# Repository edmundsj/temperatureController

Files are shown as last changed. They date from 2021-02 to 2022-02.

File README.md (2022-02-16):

# TEC Temperature Controller PCB
This PCB is designed to monitor and control the temperature of an object heated or cooled with a thermoelectric cooler (TEC), and is capable of driving up to 8A

## Features
- TEC temperature regulation within 0.1C using PI control
- Max TEC Voltage/current of 3.6V/6A when powered off 5V
- 1% settling time of ~90s 
- Bidirectional temp. control (heating and cooling) 
- 6A max current with 8-bit current monitoring (~25mA accuracy)
- Computer-independent measurement and temperature control using on-board interface
- Can be powered over USB (current limited by driving source)
- Closed-loop control of temperature using MCP9808 remote temperature sensor
- Two 3-digit 7-segment displays for temperature setpoint and measured value
- Knob potentiometer for setting target temperature
- Passive cooling (~4K/W thermal resistance) with 1.5" radial heatsink
- Arduino nano-based

Populated PCB
Fully populated PCB

Unpopulated PCB
Unpopulated, as-fabricated PCB

## Getting Started
Kicad design files for this PCB are located in the ``kicad/`` folder. Gerbers
can be generated directly for fabrication, or you can find the latest gerbers
in the ``gerbers/`` directory. The parts required can be found in ``bom.csv``.
Software can be found in the ``controller_software/`` directory, which can be
copied to your local machine, and uploaded to an Arduino nano via the Arduino
IDE. This system is rated to work at 5V, so make sure the power adapter used is
rated for 5V, and as much current as is required. For the TEC I built this
system around, that is ~6A.

## Issues
### Issues in Version 1
- [FIXED v2] Need VDD, GND connections on header going to MCP9808 board in addition to SDA and SCL.
- [FIXED v2] Need to make sure the ordering and connector matches that of the device PCB.
- [FIXED v2] In the future, a couple of accessible header GND connections would be nice, even just for probing.
- [FIXED v2] Should edit the silkscreen to include the directionality of the Arduino Nano's USB. 
- [FIXED v2] Should swap out MOSFET for a more linear BJT
- [FIXED v2] Swap out MOSFET for transistor with much lower thermal resistance
- [FIXED v2] My choice of resistor is not sufficient, the thing heats up and starts to smoke after a couple seconds at ~5A. 

### Issues in Version 2
- [FIXED v3] R4 is too close to the heatsink, difficult to access. Moved.
- [FIXED v3] Added capacitor for filtering of input drive voltage
- [FIXED v3] Added 2x2 ground header pins for probing
- [FIXED v3] Added relay with drive transistor to allow bidirectional current flow through TEC
- [FIXED v3] Added silkscreen + courtyard + mounting holes for main heatsink
- [FIXED v3] Current sensing is unreliable due to ADC being near rails, added opamp buffer + biasing

### Issues in Version 3
- Standoffs should be as far to the outside to avoid tipping the board when using screw terminals
- Need to add test piont for VDR_F. 
- C4 should be removed. We have no business filtering a voltage going to the base of the BJT.
- Add probe points for communication interface for easier debugging. 
- Add probe points for ground silkscreen
- Decouple VDD of arduino and TEC.

## Acknowledgements

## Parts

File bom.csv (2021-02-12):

Verision | Part Name | Quantity | Source | Catalog Number | Link
2 | 8.5A TEC | 1 | Digikey | 345-1740-ND | https://www.digikey.com/product-detail/en/TEC-20-33-31/345-1740-ND/9741968/?itemSeq=349654408
2 | Power NPN | 1 | Digikey | BDW42GOS-ND | https://www.digikey.com/product-detail/en/BDW42G/BDW42GOS-ND/1476196/?itemSeq=350783096
2 | 3-digit 7-segment display | 2 | Digikey | 160-1545-5-ND | https://www.digikey.com/product-detail/en/LTC-4724JR/160-1545-5-ND/408218/?itemSeq=349666458
2 | MAX7219 Display Driver | 1 | Digikey | MAX7219CWG+TCT-ND | https://www.digikey.com/product-detail/en/MAX7219CWG%2bT/MAX7219CWG%2bTCT-ND/4146791/?itemSeq=349667061
2 | Power Jack | 1 | Digikey | 839-54-00167-ND | https://www.digikey.com/product-detail/en/54-00167/839-54-00167-ND/10459295/?itemSeq=349668384
2 | Temp-Sensing IC | 1 | Digikey | 1597-1651-ND | https://www.digikey.com/product-detail/en/101020556/1597-1651-ND/9369931/?itemSeq=349671089
2 | 10K Pot | 1 | Digikey | 987-1710-ND | https://www.digikey.com/product-detail/en/P120PK-Y25BR10K/987-1710-ND/5957454/?itemSeq=349673044
2 | 2POS Screw Terminal | 1 | Digikey | 732-10955-ND | https://www.digikey.com/product-detail/en/691137710002/732-10955-ND/6644051/?itemSeq=349675219
2 | 0.2Ohm power sense resistor | 1 | Digikey | 696-1162-ND | https://www.digikey.com/product-detail/en/PF2203-0R2F1/696-1162-ND/2447810/?itemSeq=349699745
2 | Nano Headers | 2 | Digikey | S7013-ND | https://www.digikey.com/product-detail/en/PPTC151LFBN-RC/S7013-ND/810153/?itemSeq=349713274
2 | TO-220 Heatsink | 1 | Digikey | HS350-ND | https://www.digikey.com/product-detail/en/529802B02500G/HS350-ND/1216357/?itemSeq=350783079
2 | Standoff Pins | 4 | Digikey | 36-25501-ND | https://www.digikey.com/product-detail/en/25501/36-25501-ND/1532180/?itemSeq=350475444
3 | NMOS Transistor | 1 | Digikey | DMN63D8LW-13DICT-ND | https://www.digikey.com/en/products/detail/diodes-incorporated/DMN63D8LW-13/5722399
3 | 5V, 8A, 62R Relay | 1 | Digikey | G2RL-2-DC5 | https://www.digikey.com/en/products/detail/omron-electronics-inc-emc-div/G2RL-2-DC5/1789837?s=N4IgTCBcDaIOJgEoBkC0ZUBEDCBWEAugL5A
3 | MCP Dual Opamp | 1 | Digikey | MCP6L02T-E/SNCT-ND_ | https://www.digikey.com/product-detail/en/MCP6L02T-E%2fSN/MCP6L02T-E%2fSNCT-ND/2060115/?itemSeq=352014804
3 | 6Pos SMD Header | 1 | Digikey | 455-2264-1-ND | https://www.digikey.com/product-detail/en/jst-sales-america-inc/S6B-XH-SM4-TB(LF)(SN)/455-2264-1-ND/1651062
3 | 10uF 0805 cap | 3 | Digikey
3 | 100vF 0805 cap | 2 | Digikey
3 | 10k 0805 Resistor | 6 | Digikey
3 | 1k 0805 Res | 1 | Digikey
3 | 30k 0805 Res | 1 | Digikey

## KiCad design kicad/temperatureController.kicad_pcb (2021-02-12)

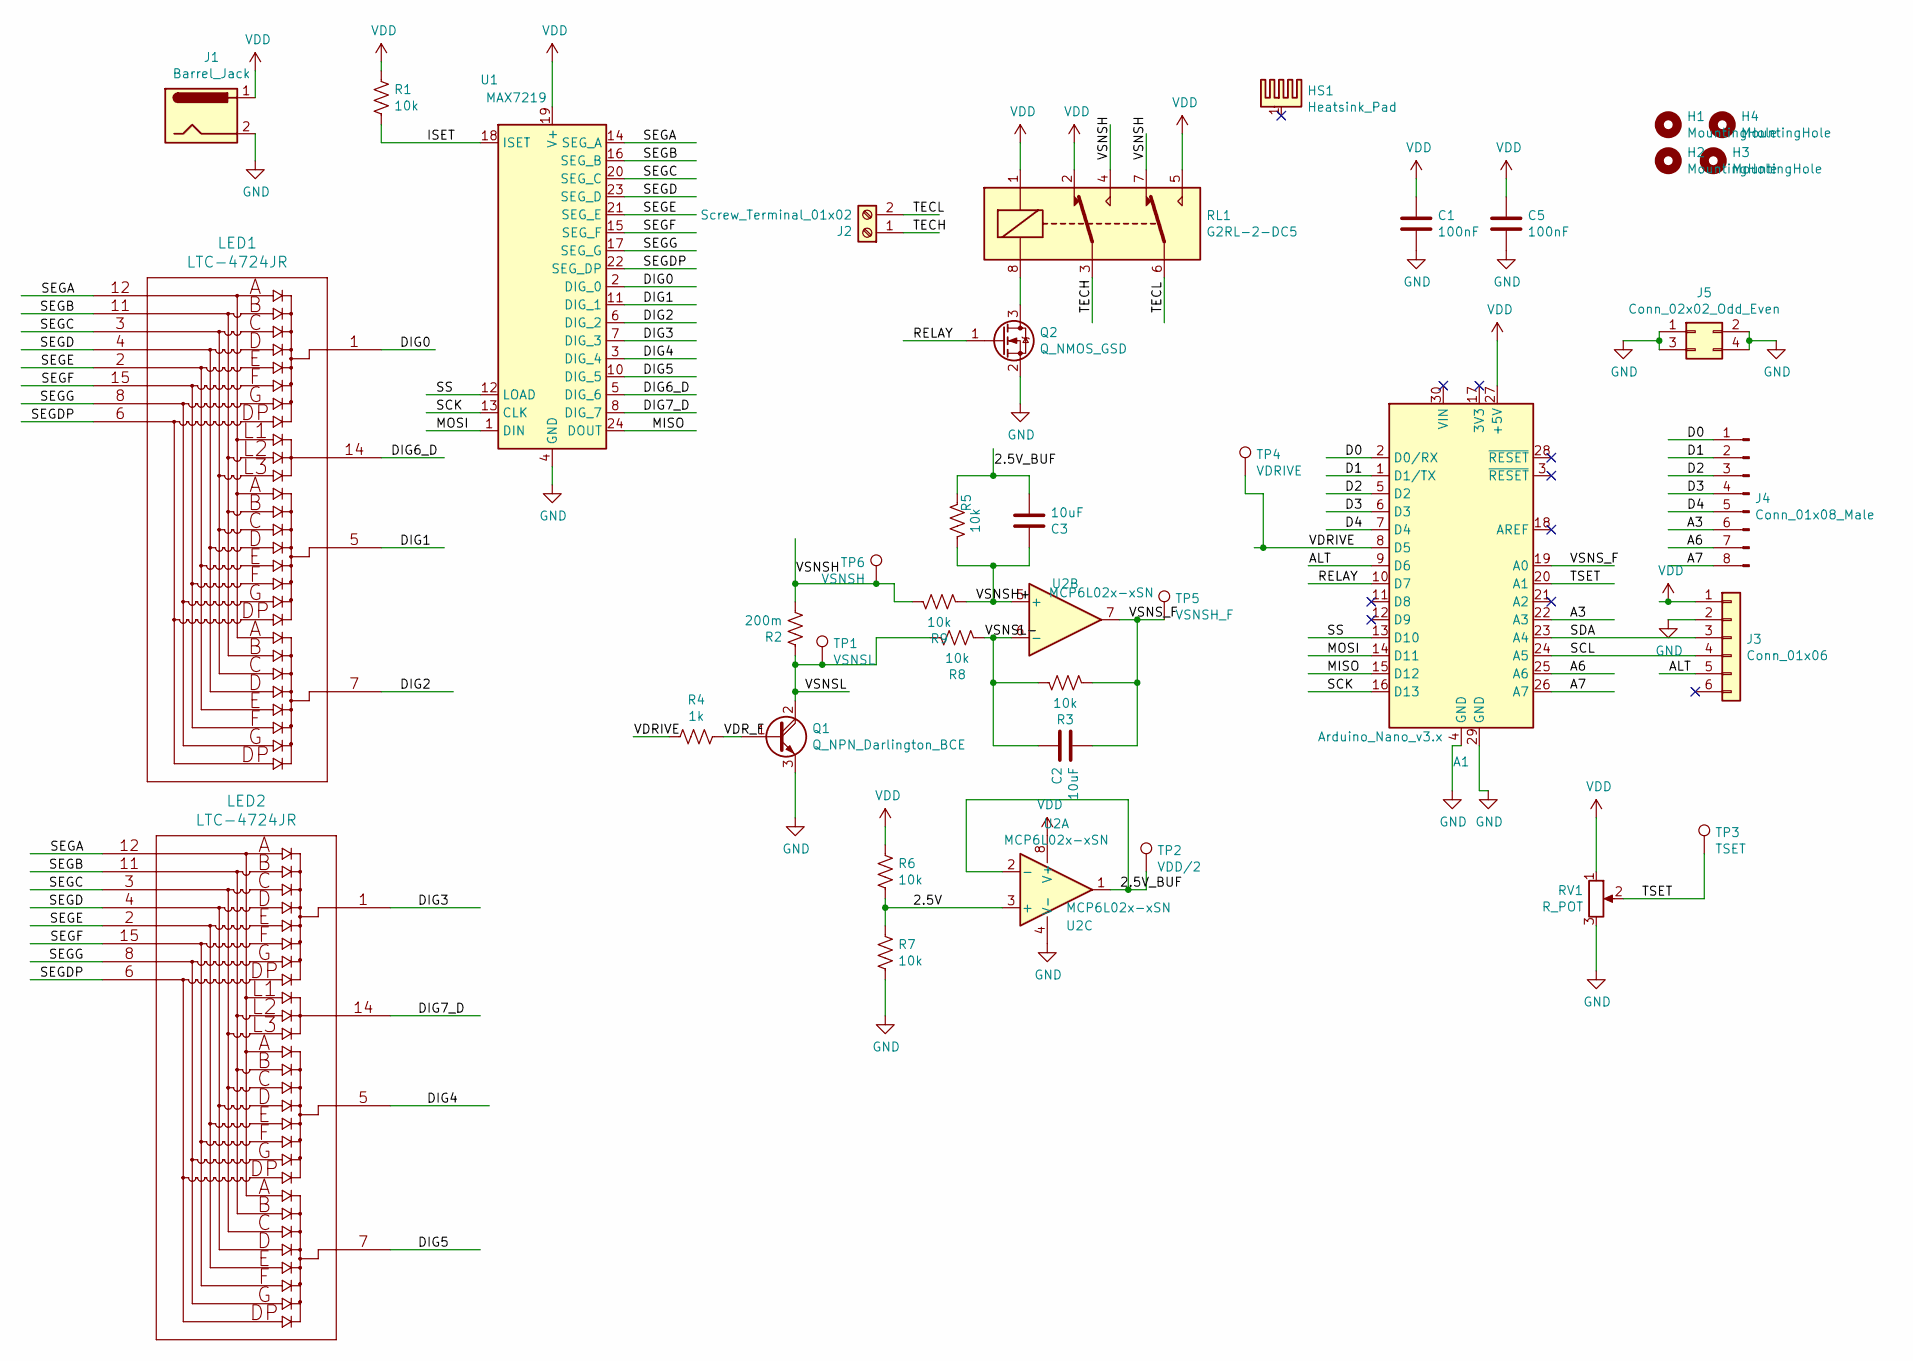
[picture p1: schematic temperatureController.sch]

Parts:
A1: Arduino_Nano_v3.x; Arduino_Nano
C1: 100nF; CP_Radial_D10.0mm_P5.00mm
C2, C3: 10uF; C_0805_2012Metric_Pad1.15x1.40mm_HandSolder
C5: 100nF; C_0805_2012Metric_Pad1.15x1.40mm_HandSolder
H1, H2, H3, H4: MountingHole; m3_mounting_hole
HS1: Heatsink_Pad; heatsink
J1: Barrel_Jack; BarrelJack_Horizontal
J2: Screw_Terminal_01x02; TerminalBlock_Altech_AK300-2_P5.00mm
J3: Conn_01x06; S6B-XH-SM4-TB
J4: Conn_01x08_Male; PinHeader_1x08_P2.54mm_Vertical
J5: Conn_02x02_Odd_Even; PinHeader_2x02_P2.54mm_Vertical
LED1, LED2: LTC-4724JR
Q1: Q_NPN_Darlington_BCE; TO-220-3_Vertical
Q2: Q_NMOS_GSD; SOT-323_SC-70_Handsoldering
R1, R3, R5, R6, R7, R8, R9: 10k; R_0805_2012Metric_Pad1.15x1.40mm_HandSolder
R2: 200m; TO-220_resistor
R4: 1k; R_0805_2012Metric_Pad1.15x1.40mm_HandSolder
RL1: G2RL-2-DC5; Relay_DPDT_Omron_G2RL
RV1: R_POT; P120PK_Potentiometer
TP1: VSNSL; TestPoint_Keystone_5000-5004_Miniature
TP2: VDD/2; TestPoint_Keystone_5000-5004_Miniature
TP3: TSET; TestPoint_Keystone_5000-5004_Miniature
TP4: VDRIVE; TestPoint_Keystone_5000-5004_Miniature
TP5: VSNSH_F; TestPoint_Keystone_5000-5004_Miniature
TP6: VSNSH; TestPoint_Keystone_5000-5004_Miniature
U1: MAX7219; SOIC-24W_7.5x15.4mm_P1.27mm
U2: MCP6L02x-xSN; SOIC-8_3.9x4.9mm_P1.27mm

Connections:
/2.5V: R6.2, R7.1, U2.3 (+)
/2.5V_BUF: C3.2, R5.2, TP2.1, U2.1, U2.2 (-)
/A3: A1.22 (A3), J4.6
/A6: A1.25 (A6), J4.7
/A7: A1.26 (A7), J4.8
/ALT: A1.9 (D6), J3.5
/D0: A1.2 (D0/RX), J4.1
/D1: A1.1 (D1/TX), J4.2
/D2: A1.5 (D2), J4.3
/D3: A1.6 (D3), J4.4
/D4: A1.7 (D4), J4.5
/DIG0: LED1.1, U1.2 (DIG_0)
/DIG1: LED1.5, U1.11 (DIG_1)
/DIG2: LED1.7, U1.6 (DIG_2)
/DIG3: LED2.1, U1.7 (DIG_3)
/DIG4: LED2.5, U1.3 (DIG_4)
/DIG5: LED2.7, U1.10 (DIG_5)
/DIG6_D: LED1.14, U1.5 (DIG_6)
/DIG7_D: LED2.14, U1.8 (DIG_7)
/ISET: R1.2, U1.18 (ISET)
/MISO: A1.15 (D12), U1.24 (DOUT)
/MOSI: A1.14 (D11), U1.1 (DIN)
/RELAY: A1.10 (D7), Q2.1 (G)
/SCK: A1.16 (D13), U1.13 (CLK)
/SCL: A1.24 (A5), J3.4
/SDA: A1.23 (A4), J3.3
/SEGA: LED1.12, LED2.12, U1.14 (SEG_A)
/SEGB: LED1.11, LED2.11, U1.16 (SEG_B)
/SEGC: LED1.3, LED2.3, U1.20 (SEG_C)
/SEGD: LED1.4, LED2.4, U1.23 (SEG_D)
/SEGDP: LED1.6, LED2.6, U1.22 (SEG_DP)
/SEGE: LED1.2, LED2.2, U1.21 (SEG_E)
/SEGF: LED1.15, LED2.15, U1.15 (SEG_F)
/SEGG: LED1.8, LED2.8, U1.17 (SEG_G)
/SS: A1.13 (D10), U1.12 (LOAD)
/TECH: J2.1, RL1.3
/TECL: J2.2, RL1.6
/TSET: A1.20 (A1), RV1.2, TP3.1
/VDRIVE: A1.8 (D5), R4.2, TP4.1
/VDR_F: Q1.1 (B), R4.1; also elsewhere on the board
/VSNSH: R2.2, R9.2, RL1.4, RL1.7, TP6.1
/VSNSH+: C3.1, R5.1, R9.1, U2.5 (+)
/VSNSL: Q1.2 (C), R2.1, R8.2, TP1.1
/VSNSL-: C2.1, R3.2, R8.1, U2.6 (-)
/VSNS_F: A1.19 (A0), C2.2, R3.1, TP5.1, U2.7
GND: A1.4 (GND), A1.29 (GND), C1.2, C5.2, J1.2, J3.2, J5.1, J5.2, J5.3, J5.4, Q1.3 (E), Q2.2 (S), R7.2, RV1.3, U1.4 (GND), U1.9 (GND), U2.4 (V-); also elsewhere on the board
unnamed: Q2.3 (D), RL1.8
VDD: A1.27 (+5V), C1.1, C5.1, J1.1, J3.1, R1.1, R6.1, RL1.1, RL1.2, RL1.5, RV1.1, U1.19 (V+), U2.8 (V+)

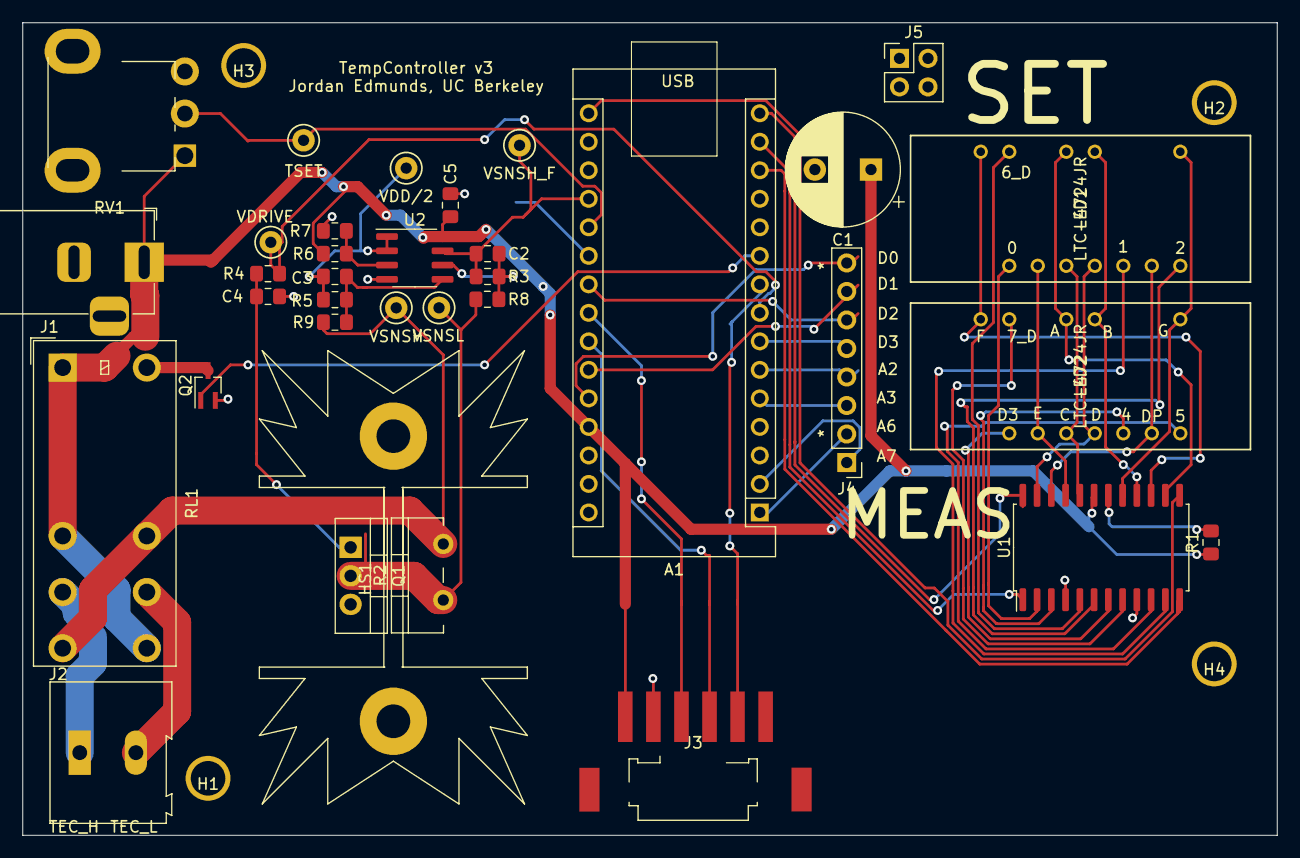
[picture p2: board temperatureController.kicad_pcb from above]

Board: 2 copper layers, 111.8 x 72.4 mm, 39 parts (0 on the bottom side), 48 nets.

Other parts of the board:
C4: 10uF; C_0805_2012Metric_Pad1.15x1.40mm_HandSolder

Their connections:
/VDR_F: C4.1; also elsewhere on the board
GND: C4.2; also elsewhere on the board

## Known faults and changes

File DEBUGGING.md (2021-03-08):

Test Data
-----------
- Version 1 is able to drive current of <100mA using closed-loop control and a 5V USB supply, but is unable to drive higher currents due to thermal runaway.
- Version 2 is able to drive at least +/- 4.5A with the main heatsink rising to 60C. TEC temperature control works over range of 1C - 80C with response time of ~10s and overshoot of 30%. 

Appendix - Debugging PCB
---------------------------
- Looks like everything fits on the PCB! I'm skeptical that the transistor can actually pump 8.5A. The datasheet says it can handle 50W, which seems bizarre. We will see how it holds up in this tiny little package.
- Now time to see how the Arduino nano handles 5V applied from both the USB and the computer. It shuold be fine b/c there's a diode separating them, essentially a 0V resistor at zero bias. Time to start writing code for this badboy.
- When driving all 6 digits, a 10k current set resistor at 3/32 duty cycle is plenty bright. I may want to keep using the 30k resistor for safety.
- The actual current measurement needs to be filtered, because there are some implausibly large measurements that occasionally smack us in the face. Our controller doesn't work well at the level of ~50mA and a load resistance of 50Ohm. It fails completely.
- Actually, this doesn't appear to be an issue with the controller, but with the sensitivity of the transistor to the unfiltered PWM. I am going to need a more aggressive filter to eliminate this, at the cost of slower dynamics. I'm going to move to a 10k resistor instead of a 1k resistor, which still gives a 100ms time constant, very fast for what I am doing.
- In the process of testing my PCB at some point the display stopped working and now all the digits are lit up, even the colons. It's unclear why this happened, but appeared to be fixed by power cycling the thing. Looks solid. I think we are ready to test on the actual TEC.
- Testing with the TEC, when injecting positive current into the red terminal, the top of the TEC definitely gets cooler than the bottom. My control system also appears to work. NEAT! Now I need to see what happens when I plug the thing in.
- NEAT! That works too!!! Looks like I can even plug it into both the computer and the power brick. It would be nice to have a power reset button so I don't have to plug anything.
- Well looks like I almost certainly fried my resistor at a forward current of ~5A. I got some magic smoke. I should definitely turn my PI controller into a PID controller. There is hella overshoot. I need to make sure that the filter is faster than the PI controller, otherwise I'm going to screw myself with overshoot. It's time to more carefully analyze the stability of this system. Once I get the current control working then I can move onto the outer temperature loop. Surprisingly the transistor seems to handle this like a champ. Might need a different resistor, though.
- Now for some reason the arduino has become inaccessible over the port I was using to communicate with it. Very odd. Too much current?
- For some reason even plugging in the high-current source makes everything freak out. 
- Time to do a high-current test. Yup, that was a miserable failure. Pretty sure I fried something. For some reason the current overshoots to ~5A and then refuses to fall back down. 

- Add a voltage divider to the gate of the transistor - we do not need more than ~4V applied to the gate. Ideally we would also convert the transistor range of ~2.5V-4V into the arduino's 0-5V. We could do this by placing the resistor at the source intsead of the drain of the transistor. This would be a good idea anyway to provide some negative feedback on our current and linearize our transfer function a little. It's possible this is an issue with the supply. I could try and apply a known voltage to the input jack.
- The weird thing is this seems to work pretty well with the USB as a power source up to ~1A, but when I use the power brick all hell breaks loose.
- It looks like the problem probably isn't with the brick, the voltage to the transistor appears to become unstable and starts to oscillate quite a bit. I think part of the issue is the noisy-ass supply
- Closed-loop control of this transistor is proving to be more difficult than I had anticipated, especially given the uncertainty of the parameters involved, and the nonlinearity of the MOSFET. The measurements are also extremely noisy and I think this is contributing to the fluctuations.
- I figured out the culprit - thermal runaway. A small (enough) amount of current heats the MOSFET, which causes the current to rise, which causes the MOSFET to heat more, and on, and on. It's not actually a problem with nonlinearity, just with the MOSFET getting too damn hot. There is instability, but it's not caused by nonlinearity - it's caused by thermal runaway of the MOSFET.
- Thermal runaway WILL be an issue with BJT's as well, since the current gain does increase with temperature (by ~a factor of 3).
- I'm probably going to want to add a small fan and choose a larger transistor package.

Version 2 Experiments
_______________________
Prediction (P): Using a proportional only controller with a value of Kp, we should see the steady-state error of the system be kp / (1 + kp), and the 95% settling time should be (1+Kp) times faster than the settling time of the filter.
Prediction (PI): Using a PI controller, we should see zero steady-state error, and for a given Kp, we should see the dynamics improve by decreasing ti (the integral time) until about wi = wL/4 * (1+Kp)^2. where wL is the frequency of the lowpass anti-aliasing filter. At this point, the characteristic frequency  of the overall system is given by wL/2 * (1+Kp) assuming zeta=1 (critical damping).
Prediction (PI): Since we are using PWM, our error will not be zero even when it *should* be zero. We have an extra sinusoid riding on top of that. This could lead to instability of the system if the anti-aliasing filter is not low-frequency enough. Specifically, we need that fL^2 * Kp^2 / (fs*fPWM) be less than 1, and we need to pray that our PWM is aliased to a reasonably high frequency compared to the sampling frequenncy. This places a restriction on Kp. and our ultimate dynamic performance, giving us a maximum natural frequency of fs*fPWM/(2*fL), where fs is our sampling frequency. For a 1Hz lowpass filter, a 1kHz PWM frequency, and a 20Hz sampling frequency, the maximum time constant we can achieve is ~20us, which means we should have plenty of margin to avoid instability.
We can create a PI controller by setting the current output at time n to equal
In = I(n-1) + Kp*(Ierr(n) - Ierr(n-1)) + wi*dt*Ierr(n)
Where I(n-1) was the previous current, Ierr is the measured minus the desired value of the current, dt is the time between samples, wi is the integral gain (in frequency form)

- When testing the TEC controller with a 10k base resistor and a multimeter to measure the current, it is able to drive up to 4A without issue. Around 4A I heard a popping sound from the TEC, and I'm not sure what caused that, but it feels very hot on both sides. I suspect I may have gone above its rated voltage. This time, though, no issues with thermal runaway, which is encouraging. It's possible the TEC is getting a higher voltage dropped across it than intended. I really need to attach it to a heatsink so I can see if it's actually cooling one side. The whole thing is definitely heating up, which should be expected. Now to stress test the whole system.
- The display output is currently pretty meaningless. 
- I really need a way of thermally connecting objects in a permanent but reversible way. Some thermal tape or something. Double-sided copper tape could actually do a reasonable job of this, where is mine? Next time I'm home I should grab the copper tapeo
- For now, I'm just going to use silver epoxy and assume the TEC will be permanently attached. I have another one if needed.

Temperature Test
___________________
- Room temp is measured to be 23.6C.
- Looks like my on-board measured current is way higher than what my multimeter is reading - it might be giving peak current and not average current? I don't know.$
- After we got above 600mA, the current started giving expected values again. I expect this is an ADC biasing issue. After increasing the current again, the measured current is again all over the place. It's down to 350mA. I might just need a better ADC.
- Now at 750mA we are measuring 210mA, this is absolute and utter nonsense. I need a better way of doing this. The present way of measuring current seems to be worse than useless. Perhaps it's an aliasing issue?
- At 1A the main heatsink isn't heating up much. Current is quite stable over time (within a few mA) less than 1A.
- Above 1A, the current is starting to fluctuate some more, +/- 20mA max.
- At 1.4A, the on-board heatsink is starting to heat up to become uncomfortably warm to the touch.
- We are able to reach a temperature differential of 45C so far at 1.5A going in the warm direction. Excellent so far. I'm going to shoot for 70C or 3.5A DC, whichever comes first.
- The current is starting to fluctuate a little more.
- At 1.6A the heatsink is still warm to the touch, but not excessively so. The measured current is 1.14A, about 50% off. I think I'm just asking way too much of the poor nano's ADC.
- At 1.9A the heat sink is getting warmer, but it's doing it's job.
- At 2.02A, I heard a weird sound I think from the TEC. This corresponded to a delta T of 63C, very close to the max rating for the TEC, so I stopped and cooled the thing down.
- The Al heatsink I attached this thing to doesn't feel significantly hotter. I am now going to change the polarity of the current.
- Room temp is measured to be 23C by an external temp sensor.
- Looks like the heatsink did heat up by ~5C during operation. I may have to pay close attention to thermal management of the TEC itself, as it is dissipating power.
- I am going to wait for the heatsink to cool down closer to 23C, then do the experiment in the reverse direction.
- The TEC appears to be broken in the reverse direction - reverse current isn't doing much at all to decrease the current. This may have been the result of my earlier mishap.
- This is not working. I'm going to go up to 2A and see what happens.
- At -3A, it only gets down to ~16C. I think it's broken.
- At -3.6A, it's down to 11C. Not nearly cold enough. I had the text facing up for this experiment.
- On the upside, the PCB has no trouble sending 3.6A, although this is as high as we can go at 100% duty cycle with a 10k resistor going to the base of the transistor. I'm going to try swapping out the TEC. Current flowing into the red wire is the problem configuration.
- Heatsink gets uncomfortably hot after a couple of minutes, nylon screw is holding, nothing is on fire.
- Above ~2A the ADC is actually quite accurate.
- The TEC appears to increase the heatsink temp during operation by ~3-4C. Time to crank up the volume, increase the current to the max rated value. Also see how my PCB handles ~6-7A. The other TEC is almost certainly damaged.
- Looks like I cannot get below ~1C due to self-heating of the TEC. At 4.25A the PCB heatsink is getting very hot to the touch, but no magic smoke. After a couple minutes the temperature is going up, now up to 3.5C. Now we're up to 5C. According to my IC, the temp is 60C at 4.2A. The current has only been reduced by ~50mA over ~10min. I can try driving the TEC even harder, up to 8A, with a smaller base resistor. I can go down to 1k. The PCB itself does not feel like it is heating up.
- The Al heatsink temp has increased to 33C from 23C. The heatsink I am using needs to do a better job staying at room temperature.
- with a Kp of 0.1, the overshoot for a target of 33.9C in heat mode was 0.8C, and it takes awhile for the controller to get down to 33.9, I suspect due to self-heating of the TEC. Larger Kp would be better.
- A Kp of 0.3 is faster with no stability issues.
- A Kp of 0.9 is even faster and has ~2C overshoot, which is very much acceptable. Let's now tune Ti.
- A Ti of 300ms is too fast - I get some instability. I should also consider restricting the current on the positive direction.
- A Ti of 700ms gives a 3C overshoot, followed by an 0.7C undershoot, followed by a 0.3C overshoot. For a 1C rise, there is a 0.3C overshoot. This is more than acceptable.

Debugging Version 3
____________________
- First, let's check whether the TEC is appropriately connected when everything is off. TEC_H should be connected to VDD, and TEC_L to VSNSH. This is indeed the case. The displays are also being driven properly, and the temperature readout is nominal (23.3C). The pot is working as well. Now time to check the voltages. VDD/2 is 2.35V, and everything else is behaving properly. Now I need to modify the code to give a readout of current.
- For some reason, there's significant nonlinearity in the current. Before we get to some threshold duty cycle, the current is very close to zero. Are we using the right transistor? A BJT should be perfectly linear.
- The current drift is also pretty extreme - from 700mA, the current is rising to over 1A without doing anything to it. This was not typical behavior on the previous board. The current continues rising, it's up to 1.2A, when I'm driving with a duty cycle of 66/255 and the heatsink doesn't feel like it's even getting warm. At least the current sensing mechanism is working :) It's accurate to within ~100mA. The current has now risen to 1.4A, and continues to rise. Now it's at 1.5A. The relay doesn't feel warm to the touch at all. The current continues to rise. Now it's at 1.7A, and the heatsink is getting considerably warmer. Turning the duty cycle down to 58/255 pushes the current down to 500mA, and now it's starting to fall. This smells like a temperature issue. But why was it not present in the last PCB? I need to measure the voltage across the drive resistor, and Vbe to see what doesn't make sense. Now the current is down to 280mA.  Now down to 150mA
- The measured voltage at the base of the transistor has a 1.1V offset, and there is a transient rise of about 100mV across our 1k resistor. This is really weird - the direction of the current appears to reverse. During duty cycling almost all the volage is dropped across the resistor. Perhaps this has something to do with the capacitor I added at the input, C4? This wasn't there before. Here's my hypothesis. It looks like the capacitor is maintaining the voltage at the base at a very high value, so what we really have is exponential (voltage from base to emitter) control of our BJT. C4 should not exist, it was a terrible idea to put it there in the first place.
- This also explains why there's so much temperature drift - we're getting the e^{-1/kT} dependence on voltage rather than the hFE vs. temperature dependence.
- Now the displays are flickering and the arduino isn't responding to commands. This is because the TEC is transiently drawing too much current during duty cycling. I will need to separate the TEC voltage supply from the arduino voltage supply in future versions. This will allow me to use other voltages and other TECs as well.
- When I connect the TEC something is making a really annoying high-frequency sound. WOAH. This appears to be due to making a connection to the TEC itself. The contact gap is making the sound. The 1k resistor looks good, it gives up to 3.5A at a voltage of ~140. Now time to implement current control and temperature control. The current also looks good, tracking the actual current within ~20mA of the actual value over the range 0-4A.
- For some reason the displays decided to have a heart attack and were all zeros. Re-uploading the code fixed this- At very low duty cycles our current measurement is not working well at all. It's oscillating all over the place. I think this is because we're now measuring a pulsed current, and our filter is not nearly aggressive enough. Personally I think we just bypass current control altogether.
- For some reason, my controlTemperature() function is crashing the arduino. Everything is hanging after that function.
- It appears to be the digitalWrite() command that is crashing the system. This is truly baffling. I can hear the relay clicking. Here's my guess - our transistor is not having a voltage applied to its gate, but we are actually applying a voltage directly to the relay. It takes up more current than our pins can drive and could potentially lock out our arduino.
- It looks like when I write the pin HIGH on a blank sheet of code, everything works just fine. There must be something conflicting with this? The serial monitor appears to be a cause of the issue.
- At 1kOhm we can drive a maximum of 4.6A of current, which gets us down to about 7.7C. The heatsink the TEC is attached to is definitely getting a little warm.
- The CPU heatsink is getting warm to the touch, we are now only able to get down to 13.3C at 4.6A. Do we want to go up in drive current? Everything here is rated for 8A, so it would be kosher. Looks like the actual temperature of the heatsink when we were driving the other side of it to 15C is at least 35C - about 12C above room temperature. If we want to get <10C, we're going to have to actively cool the CPU heatsink, either with a fan or liquid.
- The simplest way of mounting this heatsink is just to adapt the heatsink I currently have via a <25mm diameter, >1.5cm height cylinder and attach it directly to the backside of my existing cage system. I'll ask the machine shop what they have. In the meantime, I bought a fan. Should help to keep the heatsink cool.
- For a 10C positive step, the 90% rise time with Kp = 0.5, Ti = 0.7s is ~50s, and the 1% settling time is 1min50s. Let's try increasing the I. With Kp o* 0.5 and Ti of 0.3, there is a 2C overshoot and then a 1C undershoot, and the total 1% settling time is about 1min20s. Going from 30C->20C there is a 3 degree overshoot, which bottoms out by 35s and starts to increase.

* Rise time to 90% of the target value
** Settling time to within 0.1 degree of the target value, equivalent to 1% settling time.

- The temperature setpoint is drifting around like crazy, and the displays are sometimes dimming. It doesn't seem to have anything to do with the relay, but I suspect it's drift of the voltage source itself used to supply the potentiometer I'm using. This is pretty annoying and will make it more difficult to interpret results. Found the problem - the damn supply wasn't plugged in, it was using USB power.

Looks like the max current is 4.6A, which corresponds to a Vce of about 1V, a drop across our resistor of about 1V, and a drop across the TEC of 3V. The constraining factor I did not account for is Vce of the transistor.

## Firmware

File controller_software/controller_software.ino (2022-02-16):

#include <SPI.h>
#include "Seeed_MCP9808.h"
#include "displays.h"
#include <elapsedMillis.h>
#include "nano_scpi_2.h"

elapsedMillis display_time_elapsed;
elapsedMillis measurement_time_elapsed;

Display setpoint_display(DIGIT0_REGISTER, DIGIT1_REGISTER, DIGIT2_REGISTER);
Display actual_display(DIGIT3_REGISTER, DIGIT4_REGISTER, DIGIT5_REGISTER);

void setup() {
  // put your setup code here, to run once:
  pinMode(CHIP_SELECT_PIN, OUTPUT);
  pinMode(DRIVE_PIN, OUTPUT);
  pinMode(TSET_PIN, INPUT);
  pinMode(ISNS_HIGH, INPUT);
  pinMode(RELAY_PIN, OUTPUT);
  pinMode(ALT_PIN, INPUT);
    
  SPI.begin();
  Serial.begin(115200);

  // Setup the tempertature sensor interface
  initializeDisplayDriver();
  scpi.initialize();
}

void loop() {
  if(measurement_time_elapsed > SCPI::controller.sampling_time_ms) {
    SCPI::controller.control(); // chooses between temp, current, and voltage
    measurement_time_elapsed = 0;
  }

  if(display_time_elapsed > DISPLAY_REFRESH_PERIOD) {
    if(SCPI::remote_control == false) { 
      SCPI::controller.get_potentiometer_setpoint(); // gets the setpoint based on the current mode
    }
    
    setpoint_display.writeTemperature(SCPI::controller.temperature_setpoint);
    actual_display.writeTemperature(SCPI::controller.measured_temperature);
    display_time_elapsed = 0;
  }    
  if(Serial.available()) {
    SCPI::parser.ProcessInput(Serial, "\n");
  }
}

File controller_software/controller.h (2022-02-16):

#define OFFSET 0
#define ISNS_HIGH A0
#define OFFSET_CURRENT 12.0
#define CURRENT_SAFETY_LIMIT 7.0 // absolute maximum current
#define SHUTDOWN_CURRENT 5.0
#define ALT_PIN 6

#define SENSE_RESISTANCE 0.2
#define TEMPERATURE_MAX 65.0
#define TEMPERATURE_MIN -25.0
//#define TEMPERATURE_RANGE TEMPERATURE_MAX - TEMPERATURE_MIN // for some reason dividing by this does not work
#define SAMPLES_TO_AVERAGE 25
#define CURRENT_MAX 4.0
#define CURRENT_MIN -4.0
//#define CURRENT_RANGE CURRENT_MAX - CURRENT_MIN // for some reason dividing by this does not work.

#define TEMPERATURE_MODE 0
#define CURRENT_MODE 1
#define VOLTAGE_MODE 2

#define TSET_PIN A1
#define DRIVE_PIN 5
#define RELAY_PIN 7

#define TEMP_SENSOR_ADDRESS 0x18
#define TEMP_READ_REGISTER 0b0101

class Controller {
  public:
  Controller();
  uint8_t control_mode; // SCPI-settable / measurable
  bool heating_mode;

  float Kp = 70.0;
  float Kpc = 360.0; // Kp for cooling.
  float Ti_ms = 1100; // Integral time constant, in ms
  float Tic_ms = 1100; // Integral time constant going from hot->cold

  uint16_t sampling_time_ms = 20;
  
  float temperature_setpoint; // SCPI-settable / measurable
  float measured_temperature; // SCPI-measurable
  float temperature_error; 
  float previous_temperature_error;
  float filtered_temperature;
  
  float current_setpoint; // SCPI-settable / measurable
  float measured_current; // SCPI-measurable
  float current_error;
  float previous_current_error;
  float filtered_current;

  float fractional_error;
  float previous_fractional_error;

  int voltage_setpoint; // SCPI-settable/measurable

  float drive_voltage; // Actual voltage being applied to the pin
  
  float filter_coefficient;

  float temperature_accuracy; // SCPI settable/gettable

  void measure(void); 
  void measure_current(void);
  void measure_temperature(void);
  
  void control(void);
  void control_current(void);
  void control_temperature(void);
  void control_voltage(void);
  
  void get_potentiometer_setpoint(void);
  int get_potentiometer_voltage(void);
  float get_potentiometer_current(void);
  float get_potentiometer_temperature(void);

  void reset(void);

  MCP9808 sensor;
};

Controller::Controller(void) {
  MCP9808 sensor;
  this->sensor = sensor;
  this->heating_mode = false;
  this->control_mode = TEMPERATURE_MODE;
  this->temperature_setpoint = 23.0;
  this->temperature_error = 0;
  this->previous_temperature_error = 0;
  this->measured_current = 0;
  this->current_setpoint = 0;
  this->current_error = 0;
  this->previous_current_error = 0;
  this->filter_coefficient = 0.9;
  this->sampling_time_ms = 50;
  this->voltage_setpoint = 0;
  this->temperature_accuracy = 0.2;
}

void Controller::reset(void) {
  this->heating_mode = false;
  this->control_mode = TEMPERATURE_MODE;
  this->temperature_setpoint = 23.0;
  this->temperature_error = 0;
  this->previous_temperature_error = 0;
  this->measured_current = 0;
  this->current_setpoint = 0;
  this->current_error = 0;
  this->previous_current_error = 0;
  this->filter_coefficient = 0.9;
  this->sampling_time_ms = 50;
  this->voltage_setpoint = 0;
}

////////////// BEGIN CONTROL FUNCTIONS //////////////

void Controller::control(void) {
  this->measure_temperature();
  this->measure_current();

  if(this->control_mode == VOLTAGE_MODE) {
    this->control_voltage();
  }
  else if(this->control_mode == CURRENT_MODE) {
    this->fractional_error = this->current_error / (CURRENT_MAX - CURRENT_MIN);
    this->previous_fractional_error = this->previous_current_error / (CURRENT_MAX - CURRENT_MIN);
    this->control_current();
  }
  else if(this->control_mode == TEMPERATURE_MODE) {
    this->fractional_error = this->temperature_error / (TEMPERATURE_MAX - TEMPERATURE_MIN);
    this->previous_fractional_error = this->previous_temperature_error / (TEMPERATURE_MAX - TEMPERATURE_MIN);
    this->control_temperature();
  }

  if(this->drive_voltage < -255) this->drive_voltage = -255;
  if(this->drive_voltage > 255) this->drive_voltage = 255;
  
  if (this->drive_voltage <= 0) this->heating_mode = false;
  else if(this->drive_voltage > 0) this->heating_mode = true;

  if(this->heating_mode == false) {
    digitalWrite(RELAY_PIN, HIGH);
  } else {
    digitalWrite(RELAY_PIN, LOW);
  }

  if(abs(measured_current) < CURRENT_SAFETY_LIMIT) {
     analogWrite(DRIVE_PIN, int(abs(this->drive_voltage)));
  }
  else { // safety shutdown
    //analogWrite(DRIVE_PIN, 0);
  }
}

void Controller::control_temperature(void) {
  
  if(this->drive_voltage <= 0) { // We are actuating the cooling action of the TEC. Cooling dynamics are relevant
    this->drive_voltage += this->Kpc*((1 + this->sampling_time_ms / this->Tic_ms)*this->fractional_error - this->previous_fractional_error);
  }
  else if(this->drive_voltage > 0) { // We are actuating the heating action of the TEC. Heating dynamics are relevant
    this->drive_voltage += this->Kp*((1 + this->sampling_time_ms / this->Ti_ms)*this->fractional_error - this->previous_fractional_error);
  }
}


/*Implements a P-I controller for controlling the current. Currently only uni-directional: need to update. */
void Controller::control_current(void) {
  if(this->drive_voltage <= 0) { // We are actuating the cooling action of the TEC. Cooling dynamics are relevant
    this->drive_voltage += this->Kpc*((1 + this->sampling_time_ms / this->Tic_ms)*this->fractional_error - this->previous_fractional_error);
  }
  else if(this->drive_voltage > 0) { // We are actuating the heating action of the TEC. Heating dynamics are relevant
    this->drive_voltage += this->Kp*((1 + this->sampling_time_ms / this->Ti_ms)*this->fractional_error - this->previous_fractional_error);
  }
}

void Controller::control_voltage(void) {
  this->drive_voltage = this->voltage_setpoint;
}

////////////// BEGIN MEASUREMENT FUNCTIONS //////////////

void Controller::measure_temperature(void) {
  this->previous_temperature_error = this->temperature_error;
  
  this->sensor.get_temp(&this->measured_temperature);
  
  this->temperature_error = this->temperature_setpoint - this->measured_temperature;
  this->filtered_temperature = this->filter_coefficient * this->filtered_temperature +
    (1 - this->filter_coefficient) * this->measured_temperature;
}

/* Measure the current flowing through the TIA using the voltage drop across
 * an 0.2Ohm sense resistor. It also filters the current.
 */
void Controller::measure_current(void) {
  this->previous_current_error = this->current_error;
  
  int voltage_drop_reading = analogRead(ISNS_HIGH) - 0; // Our 'LOW' point is ground. Makes life easy.
  float voltage = voltage_drop_reading * 4.8 / 1023.0; // Approximate real voltage measured
  this->measured_current = voltage / SENSE_RESISTANCE - OFFSET_CURRENT;
  
  this->current_error = this->current_setpoint - this->measured_current;
  this->filtered_current = this->filter_coefficient * this->filtered_current + 
    (1 - this->filter_coefficient) * this->measured_current;
}



////////////// BEGIN POTENTIOMETER FUNCTIONS //////////////
/*
 * Measures the setpoint from a potentiometer given the mode of the controller
 */
void Controller::get_potentiometer_setpoint(void) {
  if (this->control_mode == VOLTAGE_MODE) {
    this->voltage_setpoint = this->get_potentiometer_voltage();
  }
  else if (this->control_mode == CURRENT_MODE) {
    this->current_setpoint = this->get_potentiometer_current();
  }
  else if (this->control_mode == TEMPERATURE_MODE) {
    this->temperature_setpoint = this->get_potentiometer_temperature();
  }
}

float Controller::get_potentiometer_temperature(void) {
  float total_data = 0;
  for(int i=0; i<SAMPLES_TO_AVERAGE; i++) {
    total_data += 1023 - analogRead(TSET_PIN);
  }
  
  float fractional_maximum = (total_data / SAMPLES_TO_AVERAGE) / 1023.0;
  float new_temperature_setpoint = TEMPERATURE_MIN + fractional_maximum * (TEMPERATURE_MAX - TEMPERATURE_MIN);
  
  // Add in a bit of hysteresis so that the display doesn't fluctuate
  if(abs(new_temperature_setpoint - this->temperature_setpoint) < 0.15) {
    new_temperature_setpoint = this->temperature_setpoint;
  }
  return new_temperature_setpoint;
}

float Controller::get_potentiometer_current(void) {
  float total_data = 0;
  for(int i=0; i<SAMPLES_TO_AVERAGE; i++) {
    total_data += 1023 - analogRead(TSET_PIN);
  }
  
  float fractional_maximum = (total_data / SAMPLES_TO_AVERAGE) / 1023.0;
  float new_desired_current = CURRENT_MIN + fractional_maximum * (CURRENT_MAX - CURRENT_MIN);
  
  // Add in a bit of hysteresis so that the display doesn't fluctuate
  if(abs(new_desired_current - this->current_setpoint) <= ( CURRENT_MAX - CURRENT_MIN) * 0.01) {
     new_desired_current = this->current_setpoint;
  }
  return new_desired_current;
}

int Controller::get_potentiometer_voltage(void) {
  int total_data = 0;
  for(int i=0; i<SAMPLES_TO_AVERAGE; i++) {
    total_data += 1023 - analogRead(TSET_PIN);
  }
  
  float fractional_maximum = (total_data / SAMPLES_TO_AVERAGE) / 1023.0;
  int drive_voltage = (int) (fractional_maximum * 255);
  return drive_voltage;
}

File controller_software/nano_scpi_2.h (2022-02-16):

#include "Vrekrer_scpi_parser.h"
#include "controller.h"

class SCPI {
  public: // methods
  void initialize(void);
  static void identify(SCPI_C, SCPI_P, Stream&);
  static void reset(SCPI_C, SCPI_P, Stream&);
  
  static void set_remote_control(SCPI_C, SCPI_P, Stream&);
  static void get_remote_control(SCPI_C, SCPI_P, Stream&);
  static void set_control_mode(SCPI_C, SCPI_P, Stream&);
  static void get_control_mode(SCPI_C, SCPI_P, Stream&);
  
  static void set_temperature_setpoint(SCPI_C, SCPI_P, Stream&);
  static void get_temperature_setpoint(SCPI_C, SCPI_P, Stream&);
  static void set_current_setpoint(SCPI_C, SCPI_P, Stream&);
  static void get_current_setpoint(SCPI_C, SCPI_P, Stream&);
  static void set_voltage_setpoint(SCPI_C, SCPI_P, Stream&);
  static void get_voltage_setpoint(SCPI_C, SCPI_P, Stream&);
  
  static void get_temperature(SCPI_C, SCPI_P, Stream&);
  static void get_temperature_error(SCPI_C, SCPI_P, Stream&);
  static void get_current(SCPI_C, SCPI_P, Stream&);
  static void get_current_error(SCPI_C, SCPI_P, Stream&);
  static void get_voltage(SCPI_C, SCPI_P, Stream&);

  static void measure_temperature(SCPI_C, SCPI_P, Stream&);
  static void measure_current(SCPI_C, SCPI_P, Stream&);

  static void get_ready(SCPI_C, SCPI_P, Stream&);
  
  static SCPI_Parser parser;

  // variables
  static bool remote_control;
  static Controller controller;
  
  private:
  
};

static bool SCPI::remote_control = false;
static SCPI_Parser SCPI::parser;
static Controller SCPI::controller;

static void SCPI::identify(SCPI_C commands, SCPI_P parameters, Stream& interface) {
  interface.println(F("Arduino Nano TEC Controller"));
}

static void SCPI::reset(SCPI_C commands, SCPI_P parameters, Stream& interface) {
  SCPI::remote_control = false;
  SCPI::controller.reset();
}

static void SCPI::set_remote_control(SCPI_C commands, SCPI_P parameters, Stream& interface) {
  if (parameters.Size() > 0) {
    SCPI::remote_control = (bool) (String(parameters[0]).toInt());
  }
}

static void SCPI::get_remote_control(SCPI_C commands, SCPI_P parameters, Stream& interface) {
  if (SCPI::remote_control == true) {
    interface.println('1');
  }
  else if (SCPI::remote_control == false) {
    interface.println('0');
  }
}

static void SCPI::set_control_mode(SCPI_C commands, SCPI_P parameters, Stream& interface) {
  if (parameters.Size() > 0) {
    String control_mode = parameters[0];
    if(control_mode == "voltage") {
      SCPI::controller.control_mode = VOLTAGE_MODE;
    }
    else if (control_mode == "current") {
      SCPI::controller.control_mode = CURRENT_MODE;
    }
    else if (control_mode == "temperature") {
      SCPI::controller.control_mode = TEMPERATURE_MODE;
    }
    
  }
  else if (SCPI::remote_control == false) {
    interface.println('0');
  }
}

static void SCPI::get_control_mode(SCPI_C commands, SCPI_P parameters, Stream& interface) {
  if (SCPI::controller.control_mode == VOLTAGE_MODE) {
    interface.println("voltage");
  }
  else if (SCPI::controller.control_mode == CURRENT_MODE) {
    interface.println("current");
  }
  else if (SCPI::controller.control_mode == TEMPERATURE_MODE) {
    interface.println("temperature");
  }
}

// BEGIN SETPOINT METHODS //

static void SCPI::set_voltage_setpoint(SCPI_C commands, SCPI_P parameters, Stream& interface) {
  if (parameters.Size() > 0) {
    SCPI::controller.voltage_setpoint = String(parameters[0]).toInt();
  }
}

static void SCPI::get_voltage_setpoint(SCPI_C commands, SCPI_P parameters, Stream& interface) {
  interface.println(SCPI::controller.voltage_setpoint);
}

static void SCPI::set_current_setpoint(SCPI_C commands, SCPI_P parameters, Stream& interface) {
  if (parameters.Size() > 0) {
    SCPI::controller.current_setpoint = String(parameters[0]).toFloat();
  }
}

static void SCPI::get_current_setpoint(SCPI_C commands, SCPI_P parameters, Stream& interface) {
  interface.println(SCPI::controller.current_setpoint);
}

static void SCPI::set_temperature_setpoint(SCPI_C commands, SCPI_P parameters, Stream& interface) {
  if (parameters.Size() > 0) {
    SCPI::controller.temperature_setpoint = String(parameters[0]).toFloat();
  }
}

static void SCPI::get_temperature_setpoint(SCPI_C commands, SCPI_P parameters, Stream& interface) {
  interface.println(SCPI::controller.temperature_setpoint);
}

// BEGIN MEASUREMENT METHODS 
static void SCPI::get_temperature(SCPI_C commands, SCPI_P parameters, Stream& interface) {
  interface.println(SCPI::controller.measured_temperature);
}
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

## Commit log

2021-01-05 first commit. First version to be fabricated
    [bom.csv, temperatureController-B_Cu.gbr, temperatureController-B_Mask.gbr, temperatureController-B_Paste.gbr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]
2021-01-13 added software for version 1 of PCB. Works well to control current for low currents, but thermal runaway makes the whole thing stop working
2021-01-13 updated PCB to include 60x lower thermal resistance transistor. Added space for heatsink, rearranged some components. Added 6-pin connector for temperature readout
    [temperatureController.kicad_pcb, temperatureController.sch]
2021-01-13 added gerbers for temp controller v2
    [bom.csv, temperatureController-B_Cu.gbr, temperatureController-B_Mask.gbr, temperatureController-B_Paste.gbr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]
2021-01-15 updated software to contain temperature sensor code
2021-01-19 updated README with features to make the thing readable
    [temperatureController.sch]
2021-01-23 added debugging information to README. Implemented closed-loop temperature control, tuned PI controller to have 30% overshoot and decent transient response. optimal choice of Ti might be slightly lon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
    [temperatureController.kicad_pcb]
2021-01-24 updated PCB with a relay, signal conditioning for sense resistor output. Ready to fabricate
    [bom.csv, temperatureController-B_Cu.gbr, temperatureController-B_Mask.gbr, temperatureController-B_Paste.gbr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]
2021-01-24 updated README, bill of materials with new components and capabilities. Fixed PCB to have a differential amplifier to properly bias the nano's ADC.
    [bom.csv, temperatureController-B_Cu.gbr, temperatureController-B_Mask.gbr, temperatureController-B_Paste.gbr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]
2021-01-29 updated all gerbers for version 3 of PCB. This version will be fabricated by AllPCB
    [temperatureController-B_Cu.gbr, temperatureController-B_Mask.gbr, temperatureController-B_Paste.gbr, temperatureController-B_SilkS.gbr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]
2021-02-12 tested version 3, works for bidirectional current control up to 4.6A, corresponding to a dT of 15C when one side is attached to a heatsink and actively cooled.
    [bom.csv, temperatureController.kicad_pcb, temperatureController.sch]
2021-03-08 renamed files, moved to appropriate locations
    [temperatureController.kicad_pcb, temperatureController.sch]
2021-03-08 added PCB images, basic getting started documentation. Modified features, added DEBUGGING markdown document
2022-02-16 updated arduino software, README

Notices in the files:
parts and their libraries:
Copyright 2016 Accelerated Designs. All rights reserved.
